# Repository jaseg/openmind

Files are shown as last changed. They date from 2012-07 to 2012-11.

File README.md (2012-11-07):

What is it?
-----------
OpenMind is a take on an open source electroencephalograph, i.e. a device to capture "brain waves" - the tiny electrical
signals your brain emits when working. By itself, the hardware can also be used as "just" a pretty high-resolution
albeit slow ADC to upgrade your arduino (imagine gaining 12 bits of resolution...). I suspect that the hardware should
also easily be sensible enough to directly measure muscle action potentials.

Introduction
------------
This repository contains the third version of the hardware. This is a modular system: Each PCB can (depending on what
chip you put on it and what you want to do) measure signals on one or two channels with one (absolute) or two
(differential) electrodes each. The chips used are ADS129X, 24-bit ADCs with integrated AC hum filter and preamplifier
with differential inputs. The ADS1291 contains one, the ADS1292 two channels.
In a single-channel configuration one board is the digital equivalent of a conventional EEG's active electrode.

All these "digital active electrodes" can be connected on one SPI bus with one !CS-line per module - so a bunch of eight
of them can be controlled via three SPI pins and 8 !CS pins (which themselves can be multiplexed from three pins using a
small logic IC)

Files
-----
 * `2ch-dual-shield` *recommended* A 2-channel Arduino shield which may be populated as an analog frontend for the Arduino's ADCs or (*recommended*) with an integrated analog frontend containing a 16- or 24-bit ADC.
 * `4ch-1chip-minimal-breakout` A minimalist breakout board for a large (TQFP-64) 4-channel chip. The coax electrode cables are supposed to be soldered directly to the board.
 * `4ch-dual-shield` A variant containing 4 differential channels which can be populated analog for use with the Arduino's ADC or with integrated TI frontends. This board became way too crowded, I recommend its successor, the 2-channel version.
 * `active-electrode` An active electrode design small enough so the board *can be* the electrode. In this design, the analog frontend sits on the electrode so there are no analog connections leaving the board whatsoever (except for the analog power supply, that is).
 * `analog-shield` A fully analog Arduino shield containing nil but 4 primitive differential amplifiers to connect 8 inputs to 4 adc channels of the Arduino.
 * `libraries-and-stuff` Libraries used in the boards. As of now, not all required libs are included but just the ones I made myself. For the others I still have to sort out the licensing foo.

Electrode Connections
---------------------
### Electrode modes
In absolute mode you connect one electrode to each channel's positive (non-inverting) input, and connect the negative
(inverting) input to the reference signal (as denoted on the schematic/PCB).
In differential mode you connect one electrode to each of the two inputs of each channel and the device will measure the
potential between each pair.

### Right-leg drive (RLD)
The RLD is an op-amp which is used to cancel out LF interference with the EEG signal. It works by continuously comparing
a reference potential (normally VDD/2) with an average of all electrode signals and driving a dedicated reference
electrode with the difference. This signal is very weak and thus not noticable except in the measurements.
Multiple devices can be cascaded by connecting their ``RLD_INV`` pins together and powering down all but one RLD. This
RLD's output signal is used to provide the reference voltage.
The active RLD can be selected at runtime, and you could even select the reference electrode at runtime from any
electrode connected to one of the inputs - sacrificing that one electrode.

### Lead-off detection
The ADS12XX does contain a pretty neat lead-off-detection, which can be used to measure the connection of the electrode
to the skin and the connection of the RLD electrode to the skin. This could e.g. be used to signify the electrodes
connection status with the on-board LEDs.

Miscellaneous
-------------
The ``RLDIN/RLDREF`` signal can be routed to any of the device's electrodes (whatever that might be needed for) *and/or*
any of the ADC inputs - so you can connect some auxiliary signal to this pin and measure it with any ADC.

The pad on the bottom side of the board is intended to be used to surface-mount type 261k or 269k 9v battery connectors
(available at digikey). I did not yet physically check it, but I will as soon as I order at digikey.

To guarantee galvanic separation from mains potential and to improve the power supply noise floor for the ADCs I would
recommend using a battery (rechargeable or not), radioisotope thermoelectric (or other peltier), fuel cell or other
non-switching, off-grid power supply. Extra style points are given for the radioactive option.

Software/driver
---------------
The interfacing of these ADCs is pretty straightforward. A driver for AVRs currently only supporting the ADS1194
(16-bit, 4ch version) can be found at https://github.com/jaseg/OpenMind-firmware

What to do with this?
---------------------
Just a bunch of ideas:

* http://www.instructables.com/id/Animatronic-Cat-Ears/ This only needs more pony.
* A sleep cycle-detector that wakes you up by using some LEDs to simulate dawn at *exactly* the right time
* A muscle-computer-interface, i.e. a device that senses when you physically move your muscles by measuring the pretty
  strong signals your brain sends to them. For reference see William Gibson: Burning Chrome (though, in comparision to
  the one used there, openmind is still one-way).

Warning
-------
These schematics and code are distributed in the hope that they will be useful, but WITHOUT ANY WARRANTY; without even
the implied warranty of MERCHANTABILITY or FITNESS FOR A PARTICULAR PURPOSE.
Now, the following should be obvious: Do not connect this stuff to anything alive unless you absolutely know what you are doing and do not blame me when you fry your brains with it.

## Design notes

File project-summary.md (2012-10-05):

Summary
-------
https://github.com/jaseg/OpenMind-micro
The OpenMind project aims to create easy-to-use high-quality open source EEG boards which may e.g. be used in conjunction with an Arduino to build a OpenSource EEG. We use integrated analog frontends with 24 bit precision for data acquisition.

What can I do?
--------------
Currently, we urgently need YOU to build and test the hardware and help write the host software to visualize and analyze the data.

How can I join?
---------------
Fork me on github and/or drop me a mail. Any help is welcome!

Who are the members?
--------------------
jaseg (github.com/jaseg)
meta (meta@c-base.org)

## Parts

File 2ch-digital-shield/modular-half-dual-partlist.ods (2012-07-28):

Id | Designator | Package | Quantity | Designation | Supplier and ref | Analog version | Digital Version
1 | U13 | TQFP32 | 1 | ADS1291/2 |  |  | 1
2 | U4,U5 | SO8N | 2 | INA155 |  | 2
3 | U10,U12 | SO8N | 2 | CA3140 |  | 2
4 | U1 | SO8N | 1 | TL071 |  | 1
5 | C24,C23 | SM0805 | 2 | 4n7 |  |  | 2
6 | R35,R43,R1,R56,R59,R49,R58,R2,R3,R5,R57,20k1 | SM0805 | 14 | 20k |  | 8 | 10
7 | R47,R44,R39,R36,R54 | SM0805 | 5 | 1M |  | 4 | 1
8 | C18,C15 | SM0805 | 2 | 6n8 |  | 2
9 | C19,C16 | SM0805 | 2 | 440n |  | 2
10 | R48,R40 | SM0805 | 2 | 10k |  | 2
11 | R45,R37 | SM0805 | 2 | 2k2 |  | 2
12 | C17,C14,C1,C25,C26 | SM0805 | 7 | 1µ |  | 4 | 5
13 | R4,R8 | SM0805 | 2 | LED dependent | LED series R |  | 2
14 | C2 | SM0805 | 1 | 100n |  | 1
16 | C21 | SM0805 | 1 | 10µ_ceramic |  |  | 1
17 | C22 | SM0805 | 1 | 1n5 |  |  | 1
18 | P1,P3 | PIN_ARRAY_4x1 | 2 | CONN_4 | 1 male, 1 female |  | 1
19 | SHIELD1 | ARDUINO_SHIELD_GHETTO_STACKING | 1 | ARDUINO_SHIELD |  | 1 | 1
20 | J2,J3,J4,J5,J6 | SMA | 5 | SMA |  | 5 | 5
21 | L1,L2 | Choke_SMD_Wuerth-WE-PD-Typ-M-Typ-S_RevA_27July2010 | 2 | INDUCTOR |  | 2 | 2
22 | D1,D2 | LED-0805 | 2 | LED |  |  | 2
24 | RV5,RV6 | POT_CMS | 2 | 10k |  | 2

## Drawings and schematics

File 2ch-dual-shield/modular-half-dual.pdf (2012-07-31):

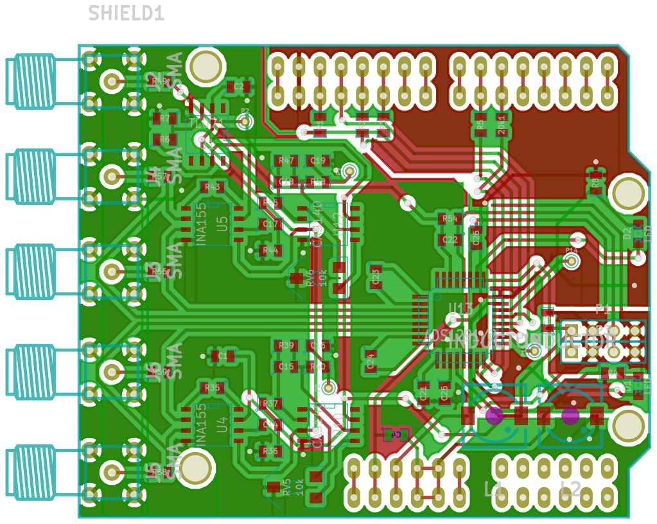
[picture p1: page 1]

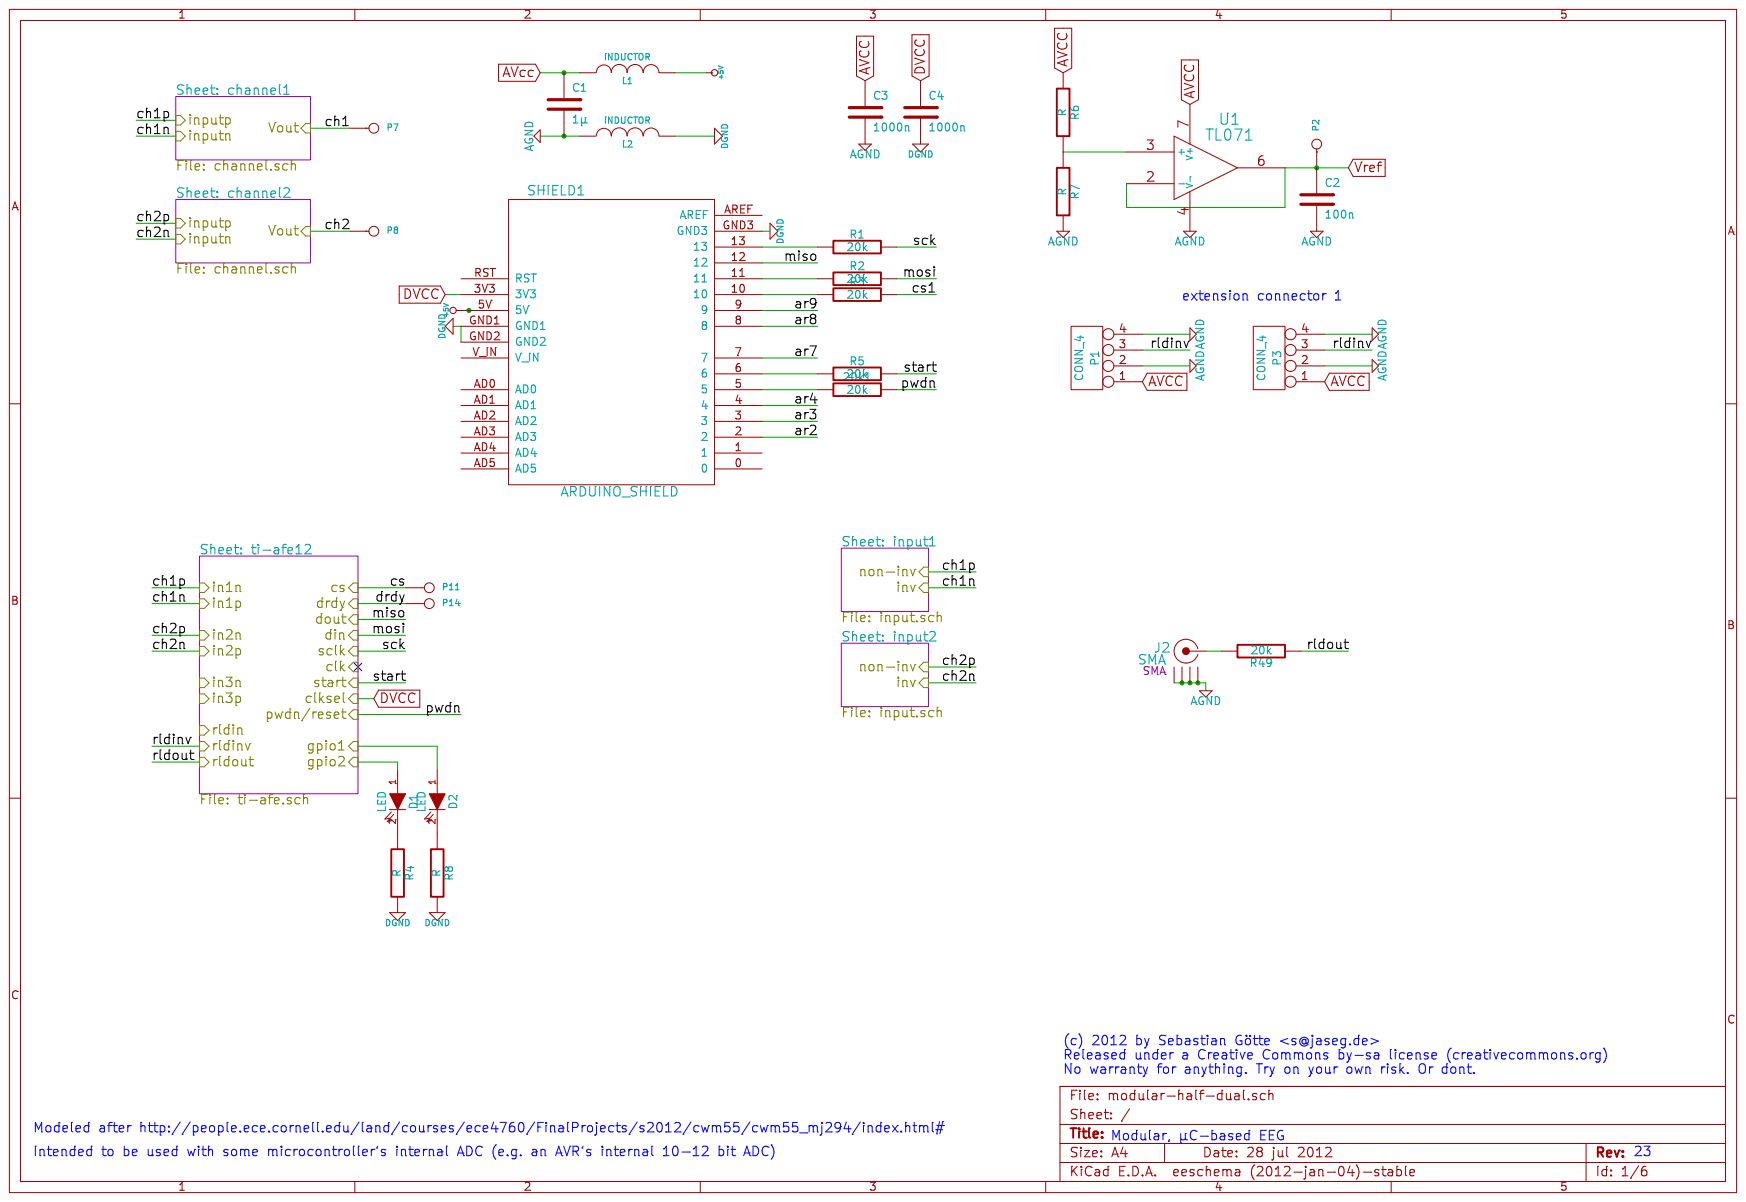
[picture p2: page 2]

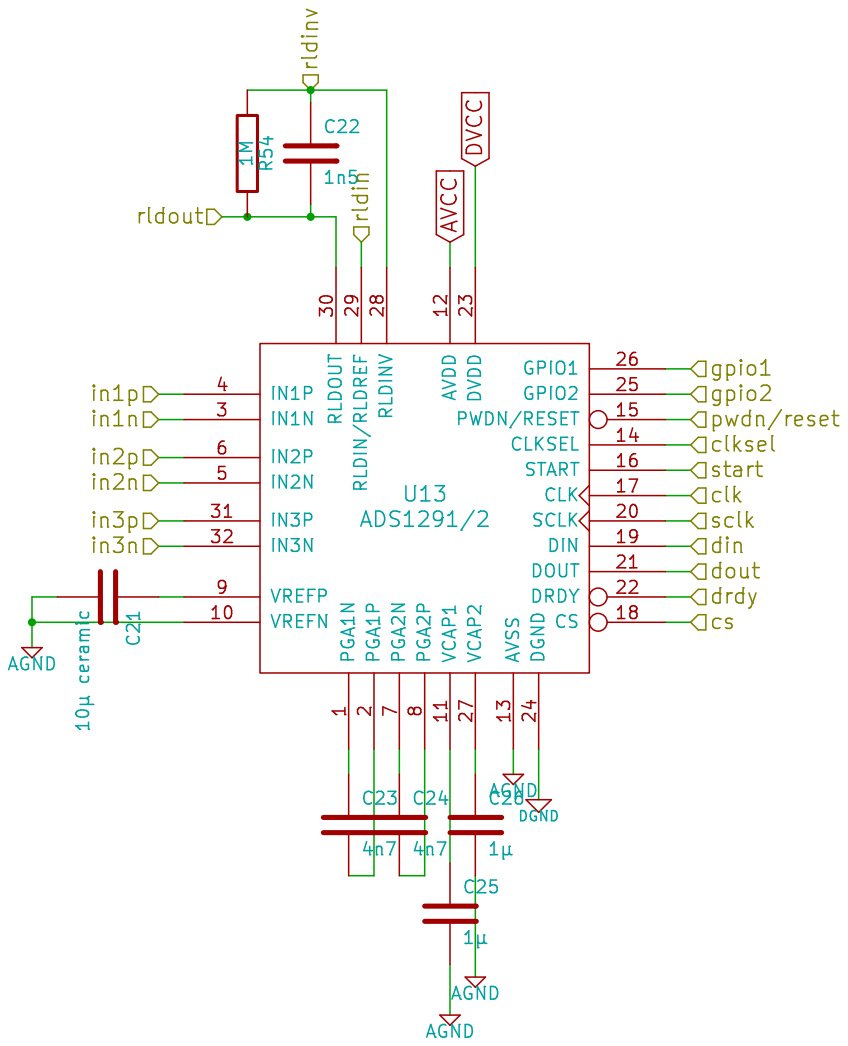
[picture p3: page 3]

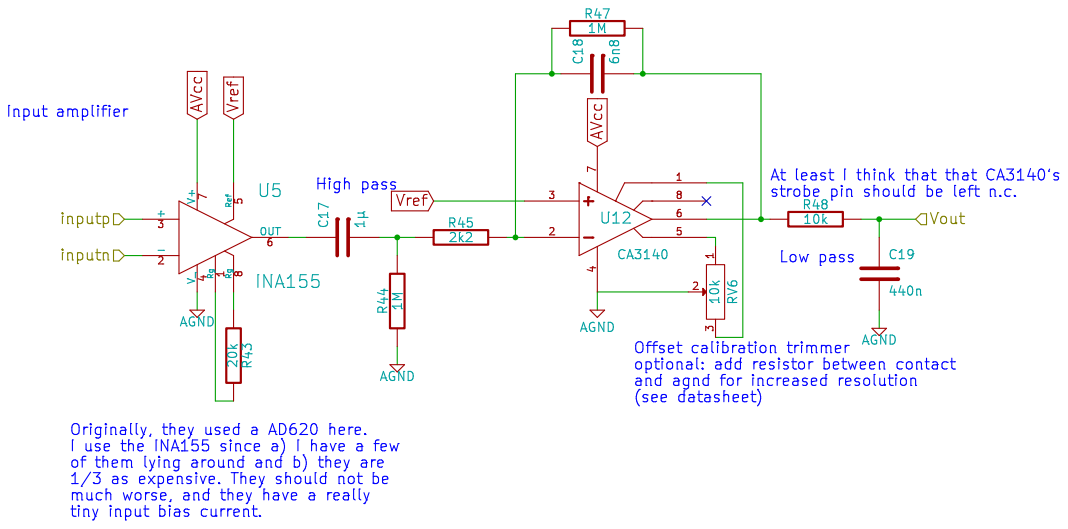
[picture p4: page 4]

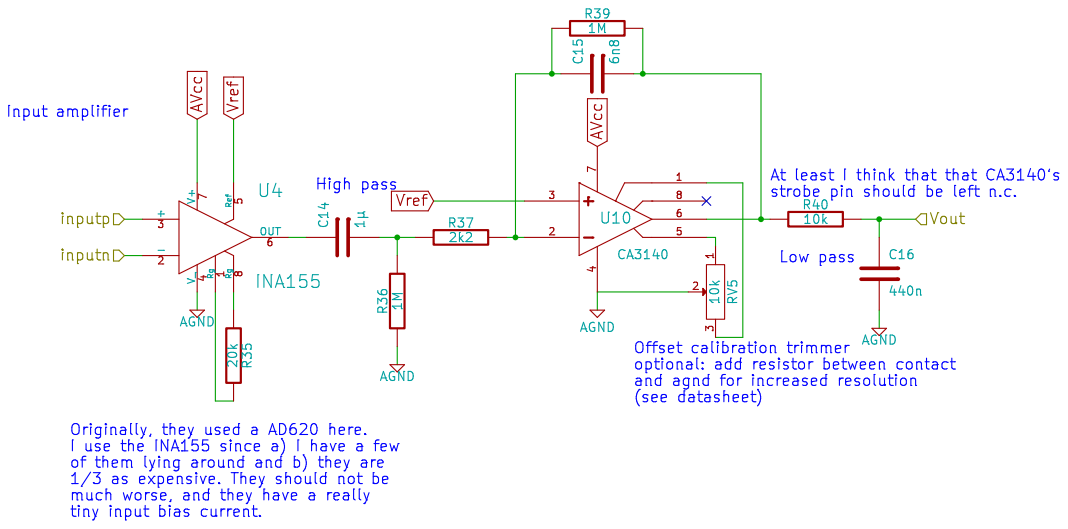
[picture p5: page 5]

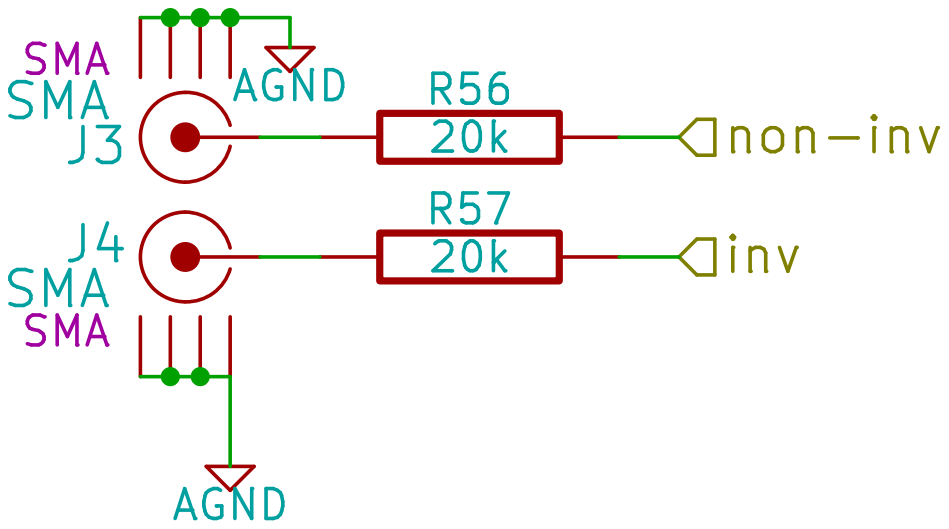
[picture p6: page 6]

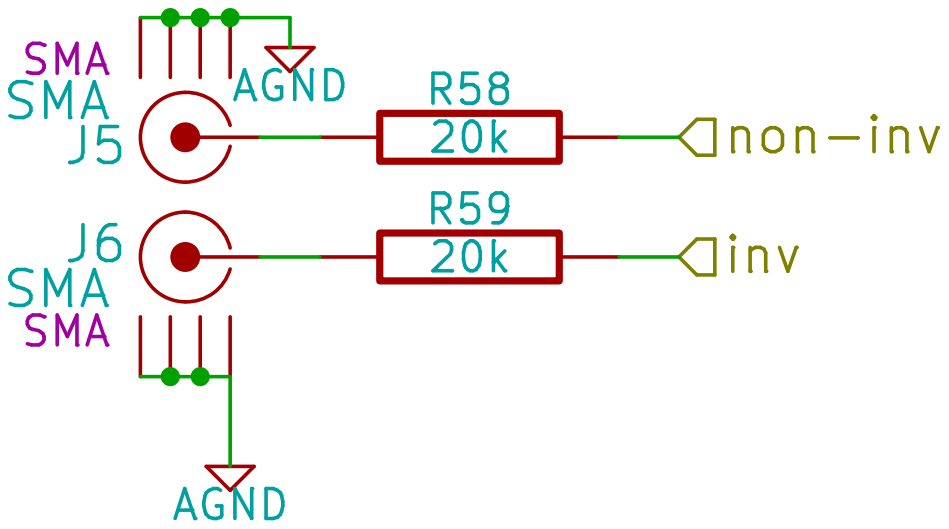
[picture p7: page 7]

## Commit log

2011-12-30 Initial commit.
    [$savepcb.brd, active.brd, active.sch, openmind.brd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]
2012-02-09 Finished the alpha pcb design.
    [active.brd, active.sch]
2012-02-10 fixed LED positions, added svg export, added copyright info and oshw logo to the pcb
    [active.brd, active.sch]
2012-02-10 Added a README
    [active.brd]
2012-02-12 Minor layout improvements
    [active.brd]
2012-02-16 Tidied up a bit
    [$savepcb.brd]
2012-02-16 Small layout changes
    [active.brd, active.sch]
2012-02-16 Added some doc
    [active.sch]
2012-02-16 small clarification in the schmematic
    [active.sch]
2012-02-16 Made some tracks wider
    [active.brd]
2012-02-20 exported the pcb
2012-02-21 Modifiied the layout to comply with 8mil track-width/spacing drcs. added the rld cascading pad.
    [active.brd, active.sch]
2012-02-28 Now DRC-compliant
    [active.brd, active.sch]
2012-02-28 Updated the readme with a note about the battery clip footprint on the bottom side of the board.
2012-02-29 Rounded the corners, moved the pads on the corners towards the center of the board for a greater corner radius
    [active.brd]
2012-04-02 Made the pads at the pcb corners larger. Made the pad clearance of the battery connector on the bottom layer larger.
    [active-Back.gbl, active-Front.gtl, active-Mask_Back.gbs, active-Mask_Front.gts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]
2012-04-02 Fixed the README
    [active.brd]
2012-05-22 Added an 100% analog arduino shield layout
    [active-Back.gbl, active-Front.gtl, active-Mask_Back.gbs, active-Mask_Front.gts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]
2012-05-25 Made a new dual arduino shield: it can be used as a simple analog frontend based on one in-amp and one op-amp per channel or it can be used with ads1292 integrated afes.
    [active.sch, channel.sch, input.sch, modular-dual.brd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]
2012-05-26 Finished the two-channel dual ti afe/pure analog-arduino adc version.
    [channel.sch, input.sch, modular-half-dual.brd, modular-half-dual.sch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]
2012-05-26 Added split ground planes
    [channel.sch, input.sch, modular-half-dual.brd, modular-half-dual.sch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]
2012-06-08 added gerber files for the 2-channel dual layout
    [modular-half-dual-Mask_Back.gbs, modular-half-dual-Mask_Front.gts, modular-half-dual-PCB_Edges.gbr, modular-half-dual.drl]
2012-07-28 Small fixes. The modular-half-dual board is final now.
    [channel.sch, input.sch, modular-half-dual-Mask_Back.gbs, modular-half-dual-Mask_Front.gts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]
2012-07-28 Added a bill of materials for modular-half-dual
    [channel.sch, input.sch, modular-half-dual.ods, modular-half-dual.sch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]
2012-07-31 Named the partslist in a sane way
    [modular-half-dual-partlist.ods, noname.sch]
2012-07-31 Split the project into one subdirectory for every board. The modular-half-dual (2ch-dual-shield) design is already converted to the new file locations (nested schematics, libraries).
    [active.brd, active.sch, channel.sch, input.sch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]
2012-07-31 Added my libraries. For the rest I still have to check the licensing stuff.
    [input.sch, ti-afe.sch]
2012-07-31 Exported the 2ch-dual-shield desgin to pdf format (board and schematics)
2012-07-31 Added a folder overview to the README and oved a folder of gerbers to the correct location.
    [active-Back.gbl, active-Front.gtl, active-Mask_Back.gbs, active-Mask_Front.gts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]
2012-10-05 Made the silkscreens pretty
    [active-Back.gbl, active-Front.gtl, active-Mask_Back.gbs, active-Mask_Front.gts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]
2012-10-05 Added the cache .libs
    [channel.sch, input.sch, modular-half-dual-partlist.ods, modular-half-dual.brd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]
2012-10-05 Cleaned up a bit. Added the contact board for the active electrode.
    [active.brd, contact.brd, modular-half-dual.brd]
